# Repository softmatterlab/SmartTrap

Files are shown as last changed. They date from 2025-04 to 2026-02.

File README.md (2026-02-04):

# SmartTrap system

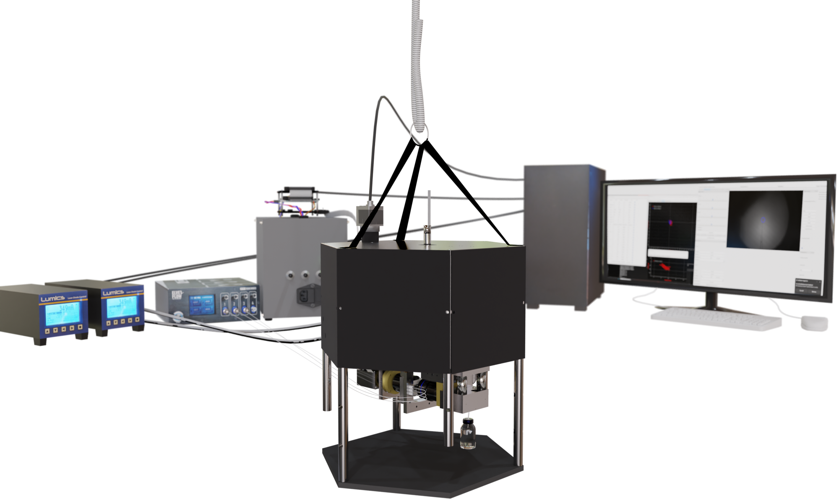
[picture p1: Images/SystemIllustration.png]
Illustration of the SmartTrap system


This GitHub page describes the SmartTrap system, including how to assemble and set up your own system.
The system is described in our publication, currently on arXiv: <https://doi.org/10.48550/arXiv.2505.05290> 
The SmartTrap system is capable of running advanced experiments such as, single molecule force spectroscopy, autonomously for over 10 hours. It can automatically trap particles and perform a growing range of measurements. Schematics and software are accessible here making it easy to build you own SmartTrap or adapt parts of it to your own system. 

## Hardware
The SmartTrap system is based on the MiniTweezers optical tweezers instrument, details of which you can find here: <http://tweezerslab.unipr.it/cgi-bin/home.pl>
Here, we provide lists of the components you need to assemble your own system along with guidlines on assembly and installation of the system.

### Components
The components of the system are split into separate units, instrument, electronics controller etc. Files listing the different components are found in the components folder.

### Assembly instructions
The assembly of the instrument is outlined in the [FullAssembly video](<Supplementary Videos/FullAssembly.mp4>). 

## Electronics
The optical tweezers instrument is controlled by a custom electronics controller. This controller consists of 3 separate circuit boards (PCBs) which are connected together via ribbon cables.

### Circuit boards
The 3 circuit boards of the controller are listed below.
- PCB 1 - Microcontroller board: Hosts the microcontroller which is an Arduino Portenta H7. This board is connected to both the other boards and the host computer.
- PCB 2 - Sensor board: This board connects to the various sensors, amplifying and digitizing the signals. Connected to the microcontroller board with a ribbon cable.
- PCB 3 - Actuator board: Connects to the motors and piezo actuators which moves the sample stage as well as the laser positions. Connected to the microcontroller board with a ribbon cable.

The Bill of Materials (BOM) files are in the [components folder](Components/) and the schematics of the boards can be found in [Instrument Schematics folder](<Instrument Schematics/>).

### Firmware
The firmware is the program running on the controller, specifically the microcontroller, to steer it. It needs to be installed for the controller to work. The files can be found in the [Firmware](Firmware/)  on this github page.
To install (flash) the firmware onto the controller do the following.

 - Connect the microcontroller to the host computer. For this use a USB-C cable.
 - Download the [Firmware folder](Firmware/).
 - Open the folder in an arduino IDE. We recommend using Arduinos own IDE which you can find here: <https://www.arduino.cc/en/software/>
 - Under tools select the arduino portenta H7 board and the correct COM port (should show up as Arduino Portenta h7).
 - Compile and upload the firmware by pressing the upload button in the top left corner of the IDE. There are a few extra packages needed to compile the software, if these are not installed the arduino IDE will automatically prompt you to install them.
Once the firmware is correctly uploaded, and the microcontroller is connected to both the controller PCB and the host computer, a green light will be flashing periodically on the microcontroller.

Note that other IDEs, such as Visual Studio Code, are possible to use, but may require a bit more work to set up.

### Controllers and drivers
The SmartTrap system combines a central instrument controller with several independent devices, each with its own hardware controller and corresponding Python driver. All drivers follow a Python protocol, so replacing hardware requires only implementing the correct interface and updating the create_devices function in the smarttrap_config.py file to use your own different device. Further details can be found in the Software folder.

- **Optical tweezers instrument** - The instrument is controlled using the custom controller. This provides also control of the motors, laser movement and sensor readings.
  - Hardware: Custom electronics controller. Controls the motors, laser positioning and reads the various photosensors.
  - Driver: Communicates with the host computer with serial USB. The different subsystems, sample stage motors, laser actuators and photosensors, are each controlled by separate classes allowing them to be easily replaced without replacing the entire controller if need be.
- **Camera** - The camera is monitored directly in the user interface. From the interface one can record videos, note that the camera feed is used in the autonomous protocols.
  - Hardware: Two options currently implemented: Thorlabs scientific cameras and Basler cameras. 
  - Driver: Connects automatically to the camera from the chosen suppliers. Other cameras can be implemented using the interface in camera_controls. The Basler cameras requires the PyPylon package while the Thorlabs cameras require installing the [thorlabs SDK](<https://www.thorlabs.com/software_pages/ViewSoftwarePage.cfm?Code=ThorCam>)
- **Laser power control** - Enables adjusting the power of the two lasers directly from the user interface as well as during autonomous protocols.
  -  Hardware: Uses an OSTech laser diode driver and TEC controller [ds11-la0.5v14-pa02v14-t8545-691](<https://www.ostech.de/en/products/laser-drivers/ds11-t85/691>).
  -  Driver: Uses serial communications, integrated in the OSTech laser.
- **Microfluidics** - The microfluidics is used to deliver particles into the system. It is possible to use manually operated syringes as well, but full digital control is necessary for autonomous procedures.
  - Hardware: Pump and valves used are from [ElveFlow](<https://elveflow.com/>), in particular the OB1 microfluidics pump and the Mux Wire V3 valve controller.
  - Driver: Requires ElveFlows proprietary software as well as the  the [LabView runtime engine](<https://www.ni.com/en/support/downloads/software-products/download.labview-runtime.html?srsltid=AfmBOoqhYo82koPNAGyVOaWM6Thr4NwTCO1KBI9eCecb0INE0mCxeVmB#569345>)
- **Micropipette** The suction of the micropipette can be toggled by activating the pump connected to it.
  - Hardware: Uses a pump powered by a dc motor, D2028B from SparkFun Electronics. This is controlled by a separate power supply, TENMA 72-2540
  - Driver: Python driver with the ability to set the power of the pump and toggle the suction on and off.
- **Motorized objective movement**- This is an optional addition and allows the user to move the objectives from the user interface for adjusting focus.
  - Hardware: Is an arduino UNO. The program for it can be found in the firmware folder.
  - Driver: Python driver communicating using serial USB. Allows for moving the objective in either long or short steps closer to or away from the chamber.
- **Pipette puller** A separate device used to make the micropipettes by heating and pulling on glass microcapillaries.
  - Hardware: Custom desgined, see pipette puller section. Powered by a TENMA 72-2540 power supply.
  - Driver: Runs in a separate graphical user interface in which the parameters of the heating can be tuned to get suitable size of the pipettes.

### Connecting the controllers
Connecting the various controllers is simple. All connect to the host computer using USB. Importantly you will need to configure the softwware to know which COM port is used for which device. This is configured in the smarttrap_config.py by updating the appropriate port, which ports are used can be found in the device manager if you are using a windows pc.

## Main program
The main program runs on the host computer and is used to steer the entire system. It includes a graphical user interface (GUI) and the fully autonomous protocols.

### Installation
To install the main program first download the files in the Software folder of the github. It is recommended to use Anaconda (<https://www.anaconda.com/>) set up a separate python environment for the SmartTrap. The system has been tested on Windows 11, compatability with other operating systems has not been tested.
The software is tested with Python 3.13 as well as a computer running Windows 11 and a CUDA ready graphics card. Older and newer versions of python will likely work if they support the required packages, but have not been extensively tested.
Once a python environment has been created, do the following to install the required packages. 
- Open a terminal in the desired environment.
- Navigate to the target folder with the downloaded files.
- Run the command: "python install_auto.py" to install the required packages.
  - Recommended: Install pytorch with CUDA support,
   - To install cuda on windows <https://docs.nvidia.com/cuda/cuda-installation-guide-microsoft-windows/> Install cuda prior to running the install command to automatically install pytorch with cuda support.

The software needs to know which device is connected to which port. To check this open up the windows device manager to check the COM ports.
Then change in the config.py file and insert the appropriate COM ports to have the software automatically connect to the devices. Note that port numbers can change, for instance if the computer is updated, if this happens just update the config file accordingly.

### Starting the software
Once the installation is complete the program is started from the command prompt with the command:
"python main.py"
This will start the program and open the graphical user interfaces. To run the command ensure that you have the correct python environment and that the command prompt is in the same folder as the software.

### Using the interface
The various controls of the instrument are divided into different by different widgets. These are essentially small windows. The most central ones are described below.

**The main window**

The main window contains the camera view as a central component and most of the different widgets are docked in it by default.
From the main window you can open the different widgets and perform various actions. By selecting the different mouse tools you can use your mouse to directly control the interfaces, by for instance selecting the motors you can click and drag on the screen to move the sample around.

**Protocols widget**

This widget is used to manually specify to the instrument which laser protocol to run. These protocols run on the microcontroller and steers the lasers, for instance moving the optical trap at a fix speed between two different positions.
To set the parameters first write in the values you want and then hit set parameters. You can see the current values of the parameters in the column to the right.
To start a protocol hit the "toggle protocol" button.

**Mouse tools**

There are several different tools you can use with the mouse to interact with the instrument based on what is seen on the camera feed. These tools are found and selected in the top left of the interface. With these you can for instance zoom in the camera view to an area of interest, measure distances, move the lasers and move the sample stage by clikcing and dragging.

**Plotting**

To plot and monitor signals, such as the forces, open a plotting window by opening the "windows" drop down menu and selecting "live plotter".
This will open the default plotting tool which plots the force along the y-axis as function of time. To change which signals are plotted click "plot 1" in the plot window to open the plot options menu. There you can find x-data and y-data. Click these to select which signal to plot on the y-axis and which to plot on the x-axis.
You can add more separate plots by clicking the "add plot" button.

There are also several plot presets which you can select directly from the windows dropdown menu in the main interfaces. These are; force PSDs, positions PSDs and force-distance X and Y. 

It is possible to export both data and graphs directly from the plotting windows. To do this right click on the plot and select the export option.

**Recording data**

To record data hit the record data button at the top right corner of the interface. It turns green automatically when data is recording.
Likewise, to record videos, hit the record video at the top left of the screen. 
You can select where to save the data by using the file drop down menu and selecting the "save data path" option. Under the "file" menu you can also select the format of videos, images and the data saved.

**Motorized stage movement**

There are two primary methods for moving the motors manually. You can use the mouse tool to move the motors by clicking and dragging, or you can use the motor control widget. From this widget you can move in your specified direction at a specific speed. The movement speed can be set by typing the desired movement speed in the entry bar or selecting one of the preset speeds.

Under the actions tab at the top of the interface you can save positions in the chamber, when you do this you also name the position. You find also the "go to saved position" option in the actions tab which lets you move to one of the saved positions.

**Laser movement**

You can manually control the laser movement from the laser movement widget. To do this use the sliders. There are 4 sliders, one per laser and axis. The sliders will also move if there is a protocol running indiciating how the lasers move. From this widget you can toggle the automatic laser alignment.

**Autonomous control**

To monitor and toggle the various autonomous protocols use the autocontroller widget. This is opened from the windows drop down menu. With the autocontroller widget you can both monitor and toggle the various autonomous protocols and use some of the autonomous subroutines (e.g. putting a particle in the pipette).

#### Testing the software

You can run the interface also without any of the devices connected. To do this follow the instructions to start the software, but add the extra argument -testmode by running the command:
"python main.py -testmode"
This will create testdrivers for the different devices which act similarily to the real devices from a software perspective, but are not connected to any physical hardware.
These testdriverds can also be used to test the functionality of just one or two devices separately from the rest of the system during development.

### Autonomous control
There are various autonomous protocols that the instrument can execute.
You can choose to run entire experiments, such as a single molecule force spectroscopy. Alternatively you can run just one of the subroutines, such as the automatic trapping.

### Neural networks
The weight of the networks needed for the automation are stored in the folder /NeuralNetworks and the weights of a pretrained network are available in the file YOLOV5Weights.pt. 
Note that other custom trained networks can be loaded directly from the user interface. 

# Expanding on the software
The software provided here is open source and as such you are free to download and modify it to your own needs.

## Adapting the software to other systems
The software suit, and in particular the interface and its back end, has been designed with the use in other system and experimental procedures in mind. 
The different protocols of the various devices simply needs to be implemented and then you need to adapt the create_devices function in config.py to ensure that your specific device is used.

## Making a sample chamber
The sample chambers used in the SmartTrap are handmade. You can make your own chambers by following the instructions below.

### Items needed
 To make a microfluidics chamber the following is needed. Below are also instructions on how to prepare the parafilm and the glass slides.
 **Tools**:
- Laser cutter
- Hotplate
- Pipette puller
- Scalpel
- Tweezers

**Consumables**:
- Parafilm
- Coverglass slides, thickness 1.5 , 60x24 mm
- Micropipette
- Channel capillaries

Note that both the parafilm and the holes in the coverglasses can be cut with a lasercutter. 

**Cutting parafilm**
First prepare the parafilm by cutting it with the laser cutter. To do this place it stretched horisontally on the laser cutter with the paper peeled off. 
You can for instance use the nescofilm roller from the tweezerlab website <http://tweezerslab.unipr.it/cgi-bin/assemblies.pl/Show?_id=ddd9> for this.

Load the pattern into the laser cutter and position it on the parafilm.
The settings of the laser cutter will depend on the model used. We use vector engraving at ca 50% of max power.

**Preparing the holes of the glass slides**
To make holes in the glass slides you can either use glass drill or a laser cutter.
The optimal settings will depend on the model of the laser cutter. Recommended is to use multiple repetitions.
If you instead use a drill carefully check that all the holes are placed in the correct position.

### Assembling a chamber
To assemble a chamber from the prepared material perform the following steps:

1. Use a scalpel to cut two pieces of parafilm free.  
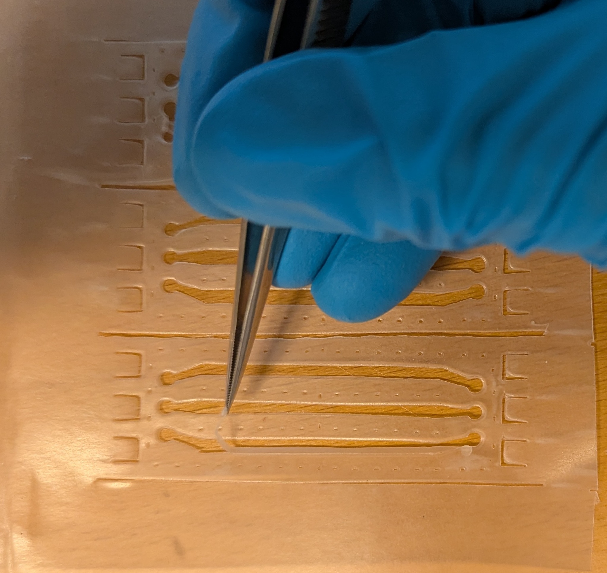
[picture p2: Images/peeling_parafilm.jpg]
Peeling away excess paraflim
   

2. Gently peel away the parafilm covering the channels using the tweezers.

3. Place the parafilm on top of a glass slide with the holes aligned on both sides as per picture.  
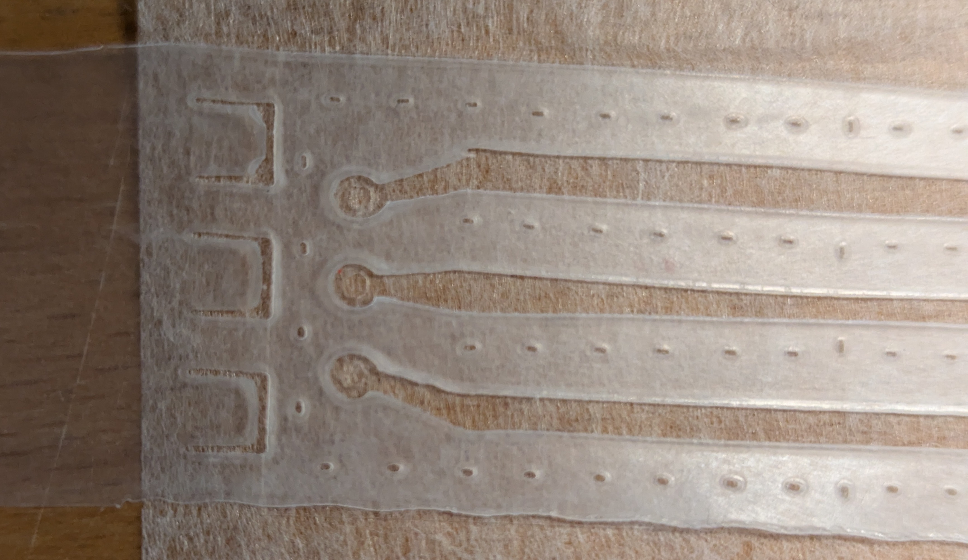
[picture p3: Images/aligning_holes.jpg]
aligning holes
   

4. At this point prepare the pipette following these steps:
   1. Place a single glass capillary centered in the pipette puller.
   2. Gently tighten the four screws to clamp the pipette tight.  
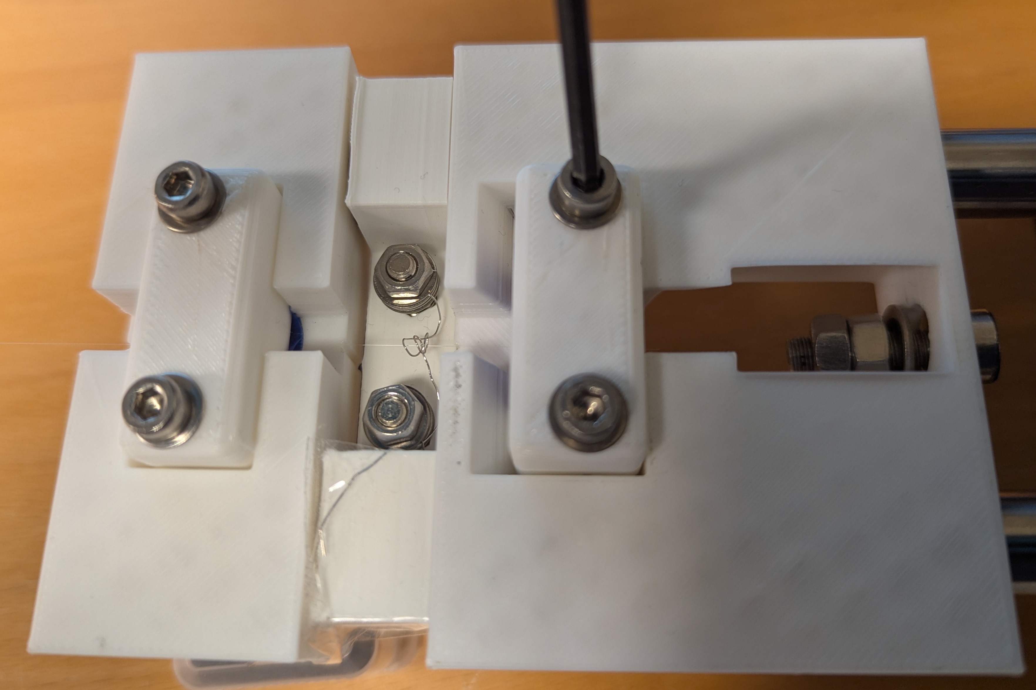
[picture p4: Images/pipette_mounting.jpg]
mounting pipette
      
   3. Carefully raise the pipette puller to a standing position.
   4. Toggle the pipette pulling protocol in the pipette puller program. [Watch demo video](<Supplementary Videos/pipette pulling.mp4>)
     NOTE: When a pipette is pulled two sharp ends are made, only the bottom part is used since the top is most often closed up completely. Therefore it needs to be cut off if the same capillary is used to make multiple pipettes. 

5. Next, place the micropipette in the center of the chamber and the capillaries next to it. Pipette and the capillary openings should be near the central chamber’s center as shown in the picture.  
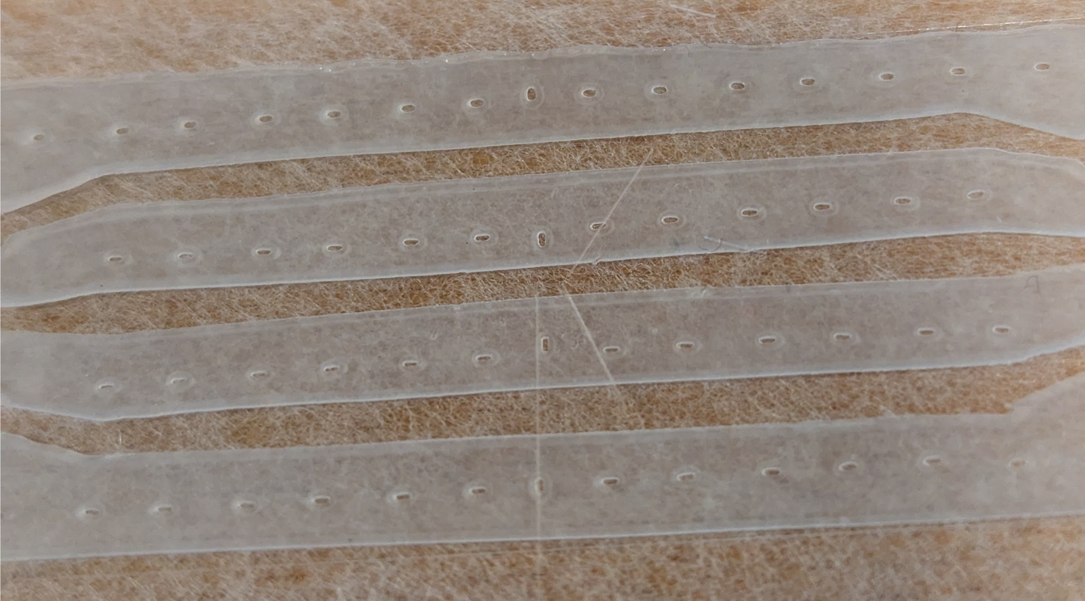
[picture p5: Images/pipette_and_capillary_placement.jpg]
pipette and capillary placed
   

6. Place the second sheet of parafilm on top of the first and align it carefully. Be careful not to move the pipette or the capillaries out of place when doing this.  
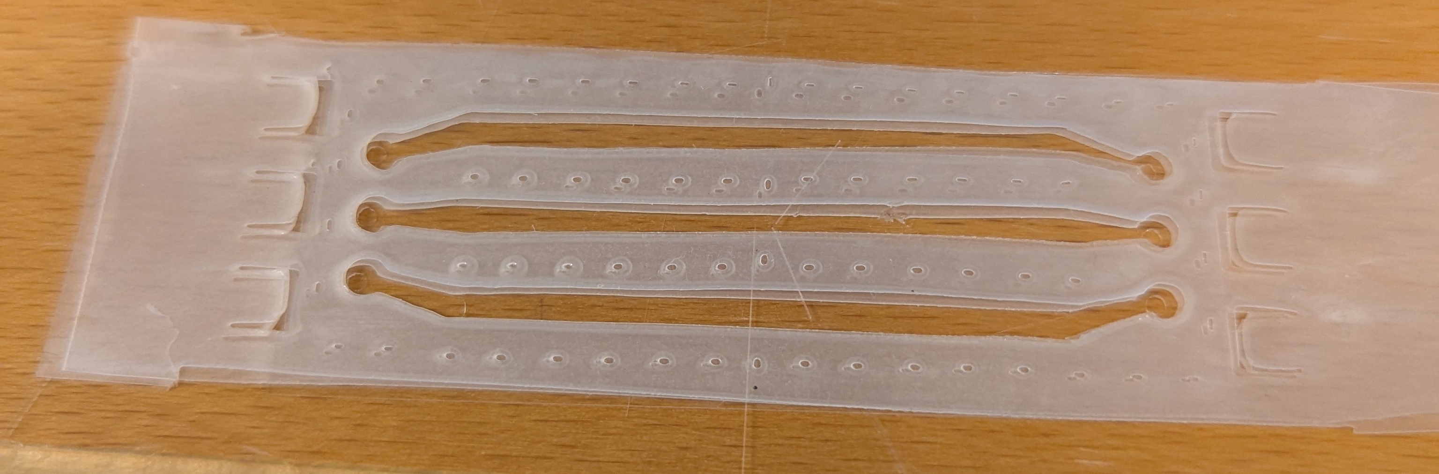
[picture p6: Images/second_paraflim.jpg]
second parafilm
   

7. Place a coverslip without holes on top and align it with the bottom slide.

8. Cut away any excess parafilm.  
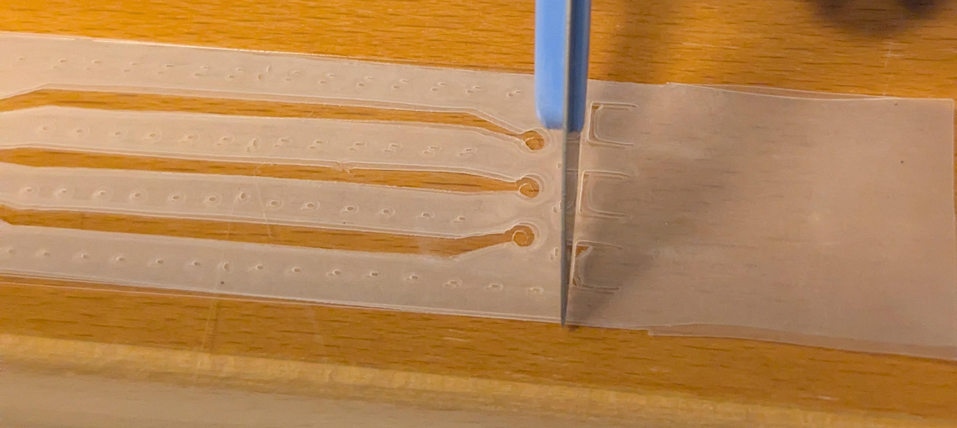
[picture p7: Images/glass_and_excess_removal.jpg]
excess parafilm removed
   

9. Heat the chamber for ~4 minutes at 110 °C on the hotplate with a weight of ~400 g applied.

10. It is recommended to sandwich the chamber between two thicker glass slides for more even weight distribution.

11. Remove the chamber and let it cool off.

### Installing a chamber
To install a chamber first take the sample holder from the system and remove the clamps before starting assembly.

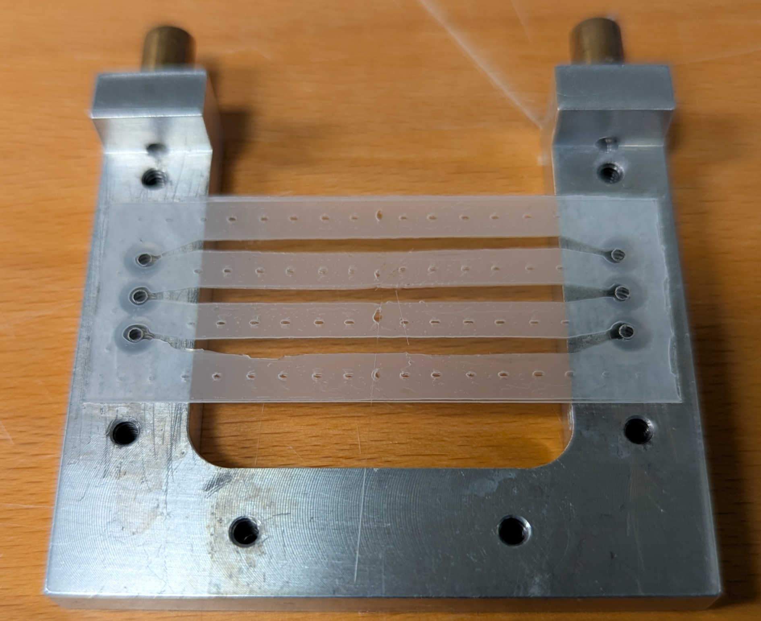
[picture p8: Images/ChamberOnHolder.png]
Chamber mounted
1. Align the chamber with the holder, ensuring that the holes of the chamber are centered at the holes of the holder. 
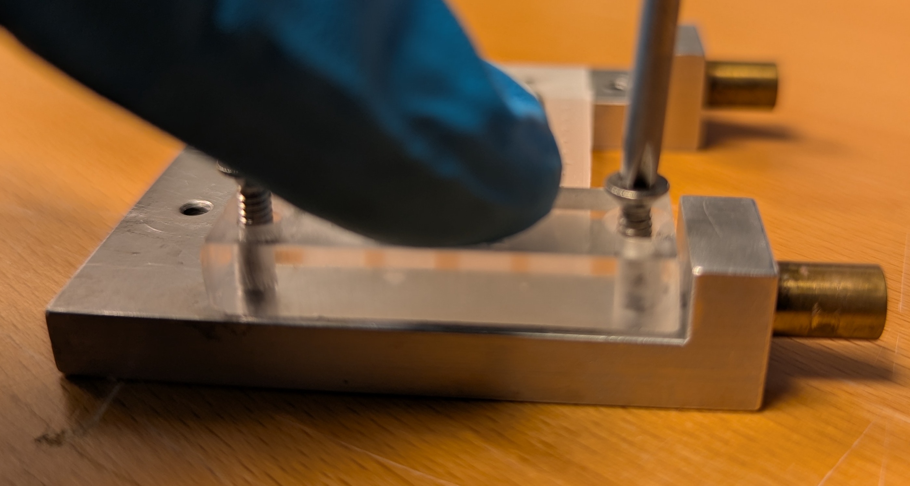
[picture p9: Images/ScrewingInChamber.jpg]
Screwing in chamber
2. Gently mount the two chamber clamps. Keep a finger on the clamp while screwing to ensure an even pressure distribution. 
3. Put the pipette clamp into position and screw the screws halfway in.
4. Put the pipette tubing under the clamp and thread the tubing around the pipette itself. Be careful so as not to break the pipette. Leave ca 5 mm of space betewen the top of the tubing and the chamber bottom.
5. Tighten the pipette clamp.
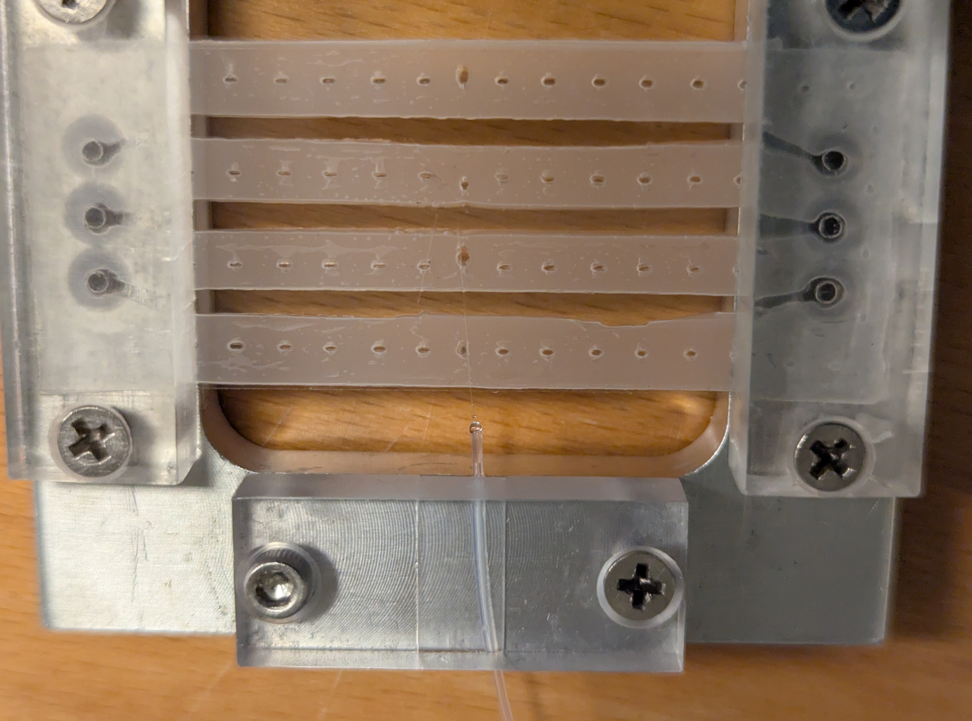
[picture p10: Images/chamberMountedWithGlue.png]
Chamber mounted and glued
6. Add a drop UV-glue to the tip of the tubing. You should be able to see a small amount of glue entering a few millimeters into the tubing. 
7. Cure the UV-glue using a UV-lamp.
8. Install the microfluidics screw connectors.
9. Connect the microfluidics tubing. Make sure the flow is directed so that the capillaries in the correct direction....
10. Flow buffer into the chamber and make sure there are no bubbles. If there are bubbles in the chamber try to remove them by briefly increasing the flow.
11. If the flow looks good, add a drop of water to the objectives of the system, push the objectives apart and put the chamber in its position as shown.

## Pipette puller
When making chambers you need a micropipette. You can make these yourself from glass capillaries using the pipette puller described here. 

### Puller assembly
Assembly instructions and list of components available in [PipettePuller](<Components/PipettePuller/>).
The puller consists of a metal base with two rods along which the pipette holder can slide.
A platina wire is heated using resistive heating to heat up the capillary and melt it.

### Using the pipette puller
To use the pipette puller first mount a glass capillary in it and connect the cables to the power supply (does not matter which cable goes where since it uses resistive heating). 
Then start the puller software by navigating to the correct folder and running the command "python pipette_puller.py". This will open up a small interface from which you can control the power supply and thereby the pipette puller heating.
The heating protocol is run by hitting the start protocol button. This will start the heating. 

The parameters used for the pulling may need to be tuned to optimize the shape of the pipette. In general, the faster the pulling the smaller the pipette opening (and the longer the larger the opening). Increasing the maximum allowed current of the puller will decrease the pulling time.

# Supplementary Videos
The /Supplementary Videos folder contains 5 videos which showcase the capabilites of the SmartTrap system.

# License
This project is licensed under the MIT License - see the LICENSE file for details.

# Cite us!
You can find more information in our paper:
<https://doi.org/10.48550/arXiv.2505.05290>
```
Martin Selin, Antonio Ciarlo, Giuseppe Pesce, Lars Bengtsson, Joan
Camunas-Soler, Vinoth Sundar Rajan, Fredrik Westerlund, L. Marcus Wil-
helmsson, Isabel Pastor, Felix Ritort, Steven B. Smith, Carlos Bustamante,
and Giovanni Volpe. SmartTrap: Automated Precision Experiments with
Optical Tweezers, May 2025. arXiv:2505.05290 [physics]
```

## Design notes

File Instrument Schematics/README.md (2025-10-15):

# Electronics of the instrument
Schematics of the controller are in the PDFs found here. Follow the steps below to connect the controller to your instrument and your controller power supply.

## Connecting the controller
The controller consists of a stack of 3 separate boards which are connected together using ribbon cables. To connect the controller follow the steps below. All the images are oriented in the same direction.
### Actuator board
Place this board on the bottom of your controller stack
- Connects to t 3 different power cables from the power supply. The 150 V (for the piezos) the, +- 15V (4 cables connector) and the 5V & 12V (3 cables connector)
- Two ribbon cables to the instrument, one for the motors (34 connectors) and one for the piezos
- Connects to the Main control board with a 34 connector ribbon cable

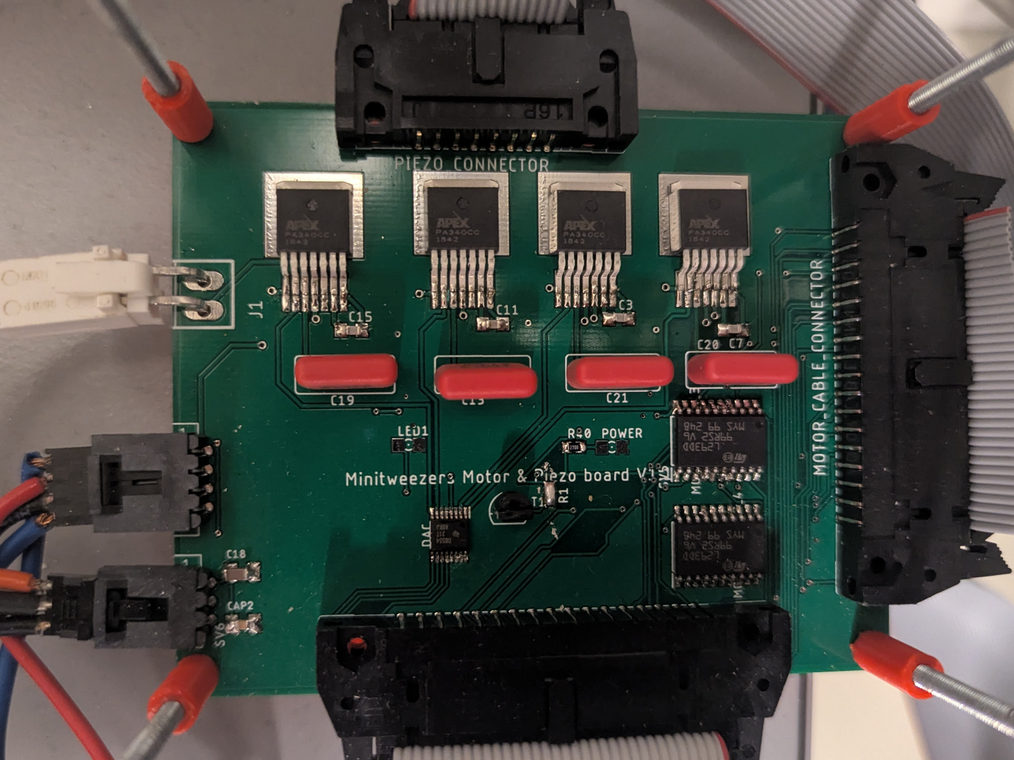
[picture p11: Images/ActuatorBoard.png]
ActuatorBoard


### Sensor board
Place this board in the middle of your controller stack
- Two power cables power it +- 15V (4 cables connector) and the 5V & 12V (3 cables connector)
- Connects to the instrument with 4 cables, one per set of PSDs, on the short end (left short end in the picture). From top to bottom in the picture these are:
  - Force B
  - Position B
  - Poistion A
  - Force A.

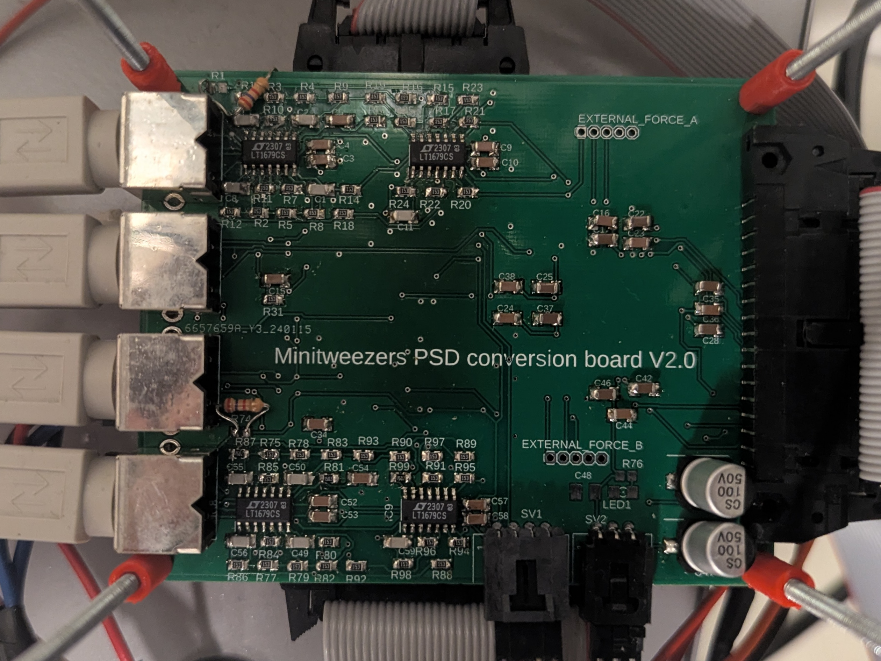
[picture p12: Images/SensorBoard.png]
SensorBoard


### Microcontroller board
Place this board on top of you controller stack.
- Connect it to the Sensor board and the actuator board using 34 connector ribbon cables. The sensor board connects to the short end of the board and the actuator board to the long end.
- Connect it to the host computer with a USB-C cable attached to the arduino portenta. The ARDUINO should be oriented as in the picture below. It will start blinking green when connected to the computer and the program is running.

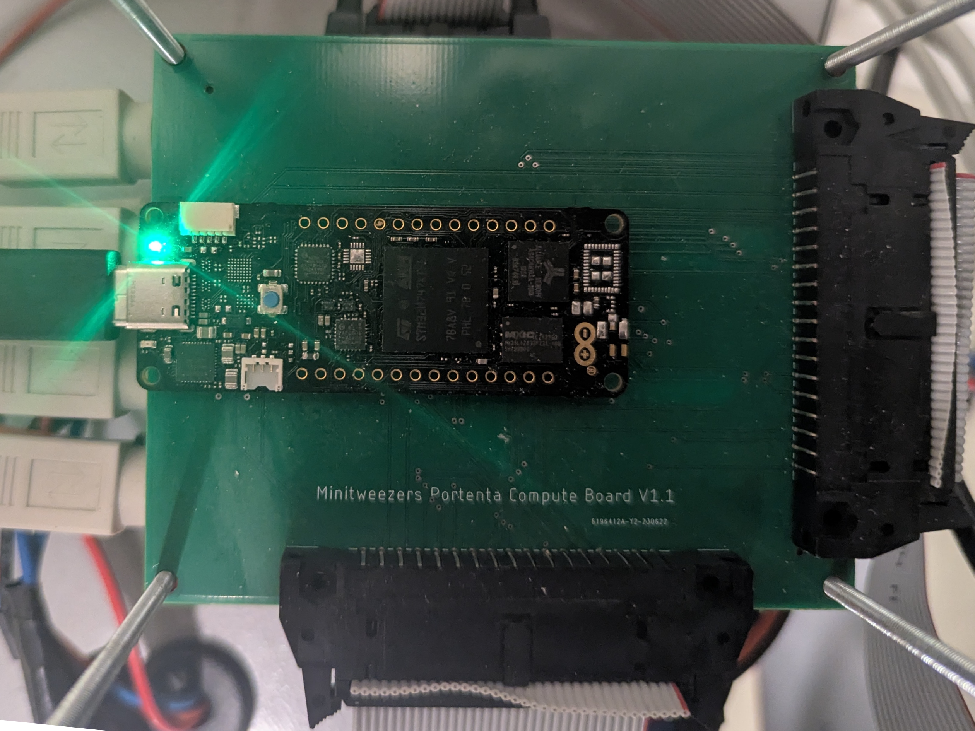
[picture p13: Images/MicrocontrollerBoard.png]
ControllerBoard


## Controller stand
To mount the controller boards you can 3D print the controller stand from the stl file ControllerStand.
It is recommended to also print the PCB spacers to put between the different PCBs. Use a set of long (ca 80 mm) M2 screws to mount the different boards and spacers effectively as in the pictures.

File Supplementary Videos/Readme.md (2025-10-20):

# Here are the supplementary videos:
The videos showcases the operation of the autonomous system.

## 1 - 3D tracking of the pipette

This video is a screen recording of the camera view in the user interface with real-time tracking visualization turned on. The video shows where the program detects the pipette and the particle. This is done while simultaneously moving the pipette with the particle in and out of focus, estimating the particle focal position.

https://github.com/user-attachments/assets/bb30b676-af74-496c-bb91-06eaeb164970

## 2 - Particle characterization 

The video shows the autonomous particle characterization being performed. The video starts with the instrument moving to a capillary to trap a particle. The first particle trapped is one of the target particles, which is determined by the autonomous algorithm based on it being larger than a certain threshold. Since it is one of the target particles the hydrodynamic radius is measured by moving it between two fixed positions in the sample while recording the forces and motor movement. Once the measurement is finished the microfluidic pump connected to the central chamber is turned on creating a flow which removes the trapped particle. Next, another particle is trapped. By chance this is a small particle, which should not be characterized, therefore it is immediately removed, again using the pump connected to the central chamber. Next, a situation in which multiple particles are trapped is shown. In this case the software detects that the focal position is offset compared to what is expected from a single particle and therefore the particles are removed even though the profile size match those of the target particles. 

Lastly, several experiments are displayed at a high speed with a timer added to illustrate how the system can run for extended times characterizing dozens of particles.

The recording is performed using the interface itself rather than recording the screen itself. This gives slightly higher video quality than a screen recording.

https://github.com/user-attachments/assets/05ffb2d9-0af1-4bef-83d9-a1c86171ede3

## 3 - Autonomous DNA pulling

Video illustrating the autonomous DNA pulling. First, a recording of a single autonomous pulling is shown starting with an empty chamber, without particles in either trap or pipette. This part of the video is commented and is a recorded camera feed showing all the different steps of the autonomous pulling process. Starting with checking the pipette, followed by trapping of the streptadavin particle and positioning of this in the pipette. This is followed by the trapping of a particle with DNA which is then attached to the particle in the pipette where after the experiment measurement is perfromed. After this first pulling, the video shows the full graphical user interface while the program performs a large number of pullings autonomously. This part of the video is shown at increased speed (to limit the duration of the video) and also the real-time plotting is shown. At the end a recording from a 10 hour continuous experiment is shown. This is shown at 600 times normal speed (10 minutes shown in 1 second) to showcase long term operation.

https://github.com/user-attachments/assets/ae2c6801-45a3-41bb-a317-445c46f49120

## 4 - Red blood cells
The videos shows how the red blood cell experiments are performed by the instrument. The video is a screen recording of the GUI and also includes a timer. After a cell has been trapped, initially at low power, cells profile is recorded in a video. Then the trapping power is briefly increased and the cell profile at higher power is recorded in another video. Thereafter the trapping power is reduced and the process repeated four more times at increasingly high powers. Thereafter the cell is removed by a flow. Since there are cells dispersed in the medium the flow is also used to bring new cells into view which are trapped and measured. If by chance there are no cells in view after flowing new medium then the flow is briefly turned on again.

https://github.com/user-attachments/assets/55d9182e-a0de-4d83-9847-974e01d260b4

## 5 - Electrostatic repulsion
Showcase of how electrostatic repulsions can be measured autonomously. When the video starts there is nothing in either trap or pipette. The program first focuses the pipette and checks its content. Next it moves to the capillary, turns on the microfluidic pump and traps a particle. The trapped particle is then placed in the pipette. After confirming that the particle has successfully transferred to the pipette, a second particle is trapped and brought to the pipette. The particle in the trap is aligned to the particle in the pipette. The trapped particle is pushed towards the particle in the pipette by moving the trap to find appropriate limits for the measurement protocol. Next the protocol and recording of data (both force and video) are started. At this stage the program zooms in on the two particles to limit the size of the videos. Once the measurement is completed, a strong flow removes both particles resetting the experiment and preparing the system for another measurement.

https://github.com/user-attachments/assets/04064912-fe21-4e13-9837-17cc39bfbc88

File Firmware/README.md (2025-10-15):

# Firmware for the arduino
This folder contains the Arduino Portenta firmware. To install download the folder and open the project in the Arduino IDE (https://www.arduino.cc/en/software/). Further instructions are available in the GitHub main page.

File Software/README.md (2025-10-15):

# This folder contains all the software needed for running the SmartTrap interface

The different modules handle different parts of the instrument controls.

To use the software with other than the default devices (e.g. a camera from a different manufacuter) implement the protocol of the corresponding device. 
These protocols need to be implemented for the different devices to work with the interface and the autonomous control functions. In the case of camera implement the "CameraProtocol" from camera_controls.py and update the create_controls function.

Below we describe briefly the functionality of the different modules. More detailed descriptions are available in the separate modules and examples of how to use them are in the Examples folder.

## install_auto
Run this file to install the packages used by the SmartTrap system.

## main
Run this file to start the program with the interface. Adding the flag -testmode will let you run it without any devices connected.

## smarttrap_interface
This contains the graphical user interface (GUI) of the smarttrap system. The entire system can be controlled using the GUI.
Contains the following two classes:
- **MainWindow** - The MainWindow is a subclass of QMainWindow and contains the main GUI.
- **ScreenWorker** - class is used to update the contents of the camera screen, displaying the camera feed and drawing things like particle markers.

### Using the software with other devices
In the create_controllers function the different devices are connected. To use your own devices, create a new create_controllers functions.

## camera_controls
Contains the classes used to interface the cameras and connect these to the user interface. Also has the functionality used to record videos.

The module contains the following classes
- **CameraClicks** - Class used to allow users to click and drag to set the area of interest of the camera. Implements the MouseTool protocol.
- **CameraMeasurement** - Used to measure distance on screen by left and right clicking. Implements the MouseTool protocol.
- **CameraProtocol** - The protocol that camera objects need to implement to function together with the rest of the program.
- **TestCamera** - A mock implementation of CameraProtocol used for testing software without any (physical) camera connected.
- **CameraThread** - A thread which runs in the background and continuously captures images using the connected camera.
- **VideoWriterThread** - Runs in the background and records videos on demand.

## data_saver
This module contains a thread saves data into files when prompted to. By running in a separate thread this limits the risk of the saving of large files interfering with other processes.

Contains the following classes:
- **SaverThreadInterface** - Interface which needs to be implemented by any DataSaver class to function with the interface.
- **DataSaverThread** - Implementation of SaverThreadInterface which is used in SmartTrap to efficiently save the data.

## control_parameters
This file contains classes and functions used to control the various devices and handle data.

Contains the following classes:
- **DataChannel** - A class which stores the data and in an array of fixed length and which can be easily, and efficiently, updated with new data.
- **ControlParametersViewer** - Wdiget which displays the current values of the various control parameters. Used primarily in development to monitor the parameters.
- **CurrentValueWindow** - Class which is a PyQT widget that is used to monitor the various data channels, their current values and an rolling average of the current values. The widget can also be used to select which channels are saved when saving.
- 

## microfluidics_controllers
This file defines the interfaces used for the 3 different microfluidics control devices; the pump, the valves and the pipette pump.
- **MicrofluidicsController (Protocol)** – Interface for multi-channel pressure controllers (connect/disconnect, set/get pressure, channel count).  
- **ValveController (Protocol)** – Interface for valve array controllers (connect, connection status, toggle/query valves).  
- **PipettePump (Protocol)** – Interface for pipette pump PSUs (connect/disconnect, power control, suction on/off, status).  
- **TestMicrofluidicsController** – Mock 3-channel pressure controller (0–2000 mbar, 1-based indexing) for testing without hardware.  
- **TestValveController** – Mock valve controller storing in-memory valve states for UI/logic testing.  
- **TestPipettePump** – Mock pipette pump PSU with % power setting and suction state simulation.  
- **MicrofluidicsMonitorThread** – QThread that syncs target/current pressures, valve states, and pipette pump power with shared state every 500 ms.  
- **ConfigurePumpWidget** – Qt form to configure channel/valve assignments and per-channel max pressures for autonomous use.  
- **MicrofluidicsControllerWidget** – Qt live control panel for setting pressures, toggling valves, and controlling pipette pump with auto-refresh.  

## motor_controls
The files defining the controls of the motors. This module defines protocol interfaces and lightweight test implementations for a 3-axis motor stage and an objective stepper, plus Qt tools/widgets for manual and mouse-driven control.

#### Protocols
- **Motor (Protocol)** – Abstract 3-axis stage motor (set/get speed, absolute move to position, velocity move, position readout, stop, is_moving).
- **ObjectiveMovement (Protocol)** – Objective actuator with slow/fast motion toward/away from the sample (connect/status + 4 directional presets).

#### Test Implementations
- **TestMotorController** – In-memory 3-axis stage with nominal speed and instant absolute moves; `move_at_speed` integrates a 1-second step for demo.
- **TestObjectiveMovement** – In-memory objective actuator that logs slow/fast moves and connection state.

#### UI & Tools
- **MotorControllerWindow (Qt)** – Manual control panel: speed presets (1/10/100 µm/s), arrow keys for x and y movement and PgUp/PgDn for Z, and a sample LED toggle bound to `c_p['blue_led']`.
- **MotorMouseMove (MouseTool)** – Mouse-driven movement: click-to-move, right-drag for X and Y velocity control, middle-drag for Z.
- **ObjectiveStepperControllerToolbar (Qt)** – Toolbar with slow/fast actions toward/away from sample for the objective stepper.

> Shared state: Components expect a `c_p` dict (e.g., `blue_led`, `mouse_params`, `camera_width/height`, `AOI`, `image_scale`, `ticks_per_pixel`), and real controllers should implement the `Motor` / `ObjectiveMovement` protocols.

## mouse_tools
This module defines a lightweight `MouseTool` protocol for PyQt/PySide applications.  
It standardizes how tools handle mouse events and optional custom drawing.

#### Protocol
- **MouseTool (Protocol)** – Abstract interface for interactive tools:
  - `mouseMove`, `mousePress`, `mouseRelease`, `mouseDoubleClick` – Mouse event hooks.  
  - `draw(qp, ...)` – Optional rendering on a `QPainter` context.  
  - `getToolName()` – Short, human-readable name of the tool.  
  - `getToolTip()` – Tooltip/description of the tool’s functionality.

## live_plots
This module provides a customizable PyQt6/pyqtgraph plotting window designed for live data visualization during operation. All the different data_channels in the data_channels can be easily plotted and monotired at will.

- **Core class – `PlotWindow`**  
  - Inherits `QMainWindow`.  
  - Manages multiple plots with per-trace metadata stored in a shared `plot_data` dict (`x`, `y`, `pen`, `L`, `sub_sample`, `averaging`).  
  - Updates plots on a `QTimer` loop (`update_plot_data`) pulling from a user-provided `data` mapping.  
  - Designed for `data[key]` objects exposing:  
    - `.get_data(n)` / `.get_data_spaced(n, step)`  
    - `.unit` (for axis labels)  
    - `.index` (for alignment logic).  

- **Supporting dialogs**  
  - `PlotAxisWindow` – manual x/y axis bounds.  
  - `PlotLengthWindow` – number of points retained per trace.  
  - `PlotSubsamplehWindow` – subsampling/averaging interval per trace.  

- **Customization hooks**  
  - Per-trace styling: line color, marker symbol, symbol color.  
  - Background color presets.  
  - Aspect ratio locking.  
  - Non-overlapping averaging helper (`non_overlapping_average`).  

- **Programmer notes**  
  - Plots are registered dynamically with `add_plot(x_key, y_key)`.  
  - Each plot can be removed via `delete_plot(idx)`.  
  - Menus are auto-rebuilt from `plot_data` state (`create_plot_menus`).  
  - Designed to integrate with an external control dict (`c_p`) that tracks program state (e.g. `c_p['program_running']`).  

This structure makes it easy to embed real-time plotting into larger control/analysis pipelines while keeping plotting logic isolated and extensible.

## real_time_tracking
This module defines a protocol for particle and pipette tracking (ObjectTracker) together with a simple test implementation (TestTracker) and a PyQt-based control widget (TrackingControlWidget).
This provides both the interface layer and a test harness for integrating tracking models into the larger system.

Contains the following classes:
- **ObjectTracker** - A protocol specifying the expected interface for tracking backends (frame analysis, particle and pipette detection, z-position prediction, and model loading).
- **TestTracker** - A mock tracker that generates random particle positions and simulates pipette detection, useful for testing the GUI without real models.
- **TrackingControlWidget** - Qt widget for toggling tracking modes, loading 2D/z models, and adjusting z-offsets during experiments.

## laser_protocols
The laser protocols define various protocol used to move the lasers in a controlled manner and thereby execute various experimental protocols.
This module defines a common `ExperimentLaserProtocol` interface and several concrete laser-control protocols, plus a Qt widget for selecting, configuring, and running them.

#### Protocol Interface
- **ExperimentLaserProtocol (Protocol)** – Unified API for start/stop/run state, human-readable names/descriptions, and numeric parameters (with descriptions, tooltips, and limits).

#### Protocols
- **ConstantSpeedProtocol** – Moves a laser along a chosen axis at constant speed between two position limits.  
- **Push2ForceProtocol** – Pushes a trapped particle in a given direction until a target force is reached, then stops.  
- **ConstantForceProtocol** – Maintains constant force along X/Y by auto-aligning the second trap and updating force setpoints.  
- **ForceLimitProtocol** – Sweeps between lower/upper force limits at a set speed, reversing direction when thresholds are crossed.  
- **PushAndWaitProtocol** – Pushes toward a force limit, waits for a set duration, then transitions to pulling based on position/force bounds.

#### UI
- **PullingProtocolWidget (Qt)** – Dropdown to pick a protocol, per-parameter editors (labels, tooltips, limits, current values), and a toggle to start/stop; refreshes at 40 ms to call `run_protocol()` while active.

## auto_controller
In this module all the autonomous protocols are defined as well as the corresponding user interface elements. 

- **AutoControllerThread** - Thread which runs the autonomous protocols. This also handles the real-time tracking to simplify synchronization.
- **AutoControlWidget** - A QWidget used to control and monitor the various autonomous protocols. Can also be used to toggle the subroutines which build up the autonomous protocols such as particle trapping.
- **StokesTestWidget** - A small QWidget used to perform the stokes which can be used to calibrate the force detectors or to measure particle diameters.
- **SelectLaserPosition** - A MouseTool used to indicate in the camera feed where the two lasers are. This in turn is used by the autonomous protocols to determine if a particle is trapped or not.
- **AutonomousProtocol** - Interface used for the autonomous protocols. Currently the following protocls are implemented:
  - **DNAPulling** - Autonomous DNA pulling protocol implementing the AuotonomousProtocol.
  - **ElectrostaticRepulsion** - AutonomousProtocol which measures repulsive forces between two charged particles.
  - **ParticleCharacterization** - AutonomousProtocol. Selects a particle within a certain size range (as estimated by the real-time tracking) and measures its hydrodynamic radius using a stokes test.
  - **RBCStretching** - AutonomousProtocol used to measure the stretching of red blood cells by trapping them at various laser powers.

# SmartTrap minitweezers instrument specific files
Certain devices are specific to the SmartTrap system and thus rely on the specific hardware, e.g. specific microfluidics pump.
To use these devices they implement the protocols specified in the above files. By default these are the devices loaded by the program using the create_devices function from the smarttrap_config.py file.

## smarttrap_driver
This module contains the classes that handles communications to and from the SmartTrap electronics controller. Specifically a class which only handles the serial communications running in a separate process and a monitoring thread which parses the commands sent to and from the instrument. During operation both these are running continously.

## basler_cameras
Contains the BaslerCamera class which is an implementaion of the CameraProtocol which can be used with cameras from Basler. Comparible with any camera from Basler which connect using USB. Uses the pypylon package for controlling the camera.

## thorlabs_scientific_cameras
Contains the ThorlabsScientificCamera class which is an implementaion of the CameraProtocol which can be used with cameras from Thorlabs.
To use this you need to have the thorlabs scientific camera sdk installed see <https://www.thorlabs.com/software_pages/ViewSoftwarePage.cfm?Code=ThorCam>

## elvesys_pump
Contains an implementation of the microfluidics controllers that work with the OB1 micrfluidics controller from elvesys as well as their microfluidics valve.

## OSTech_laser_controller
Implementations of the lasercontroller that work with laser current drivers from OSTech.

## smarttrap_tracker
The default tracking used in the SmartTrap system. Here the real-time tracking interfaces is implemented to work with yolov5 and the convoluitonal neural network that monitors the z-position.

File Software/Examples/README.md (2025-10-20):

# These are examples of how use the various devices
The examples provide minimal codes for testing the various devices and interfaces. The various files shows how to connect to the various devices and execute basic commands, e.g. taking a picture with the camera.

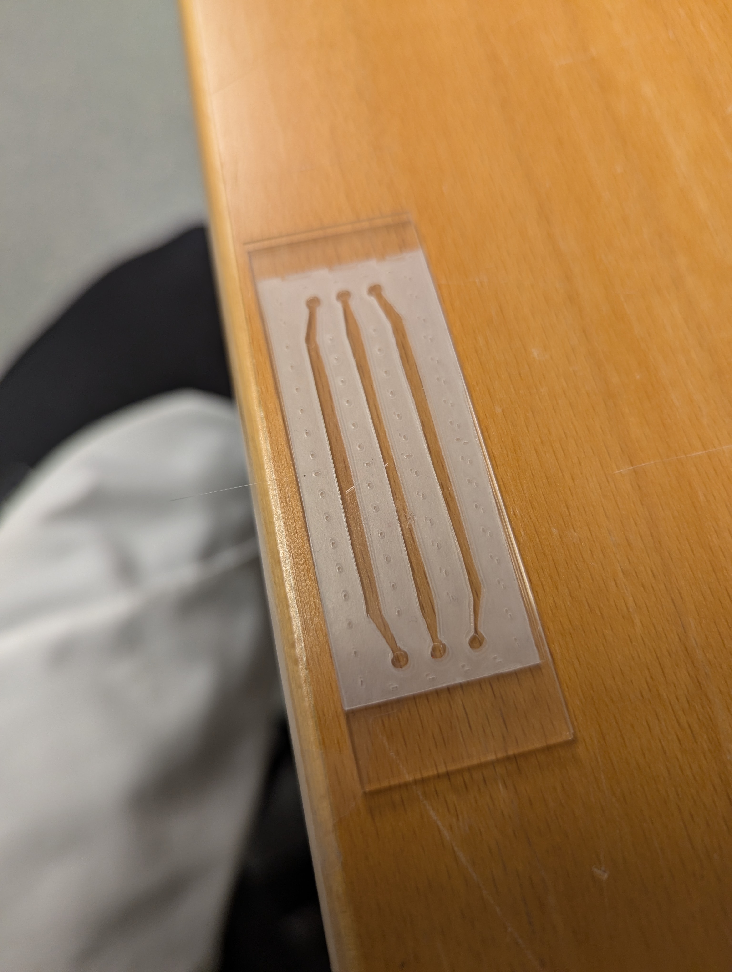
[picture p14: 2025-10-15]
Images/chamber_in_glass.jpg

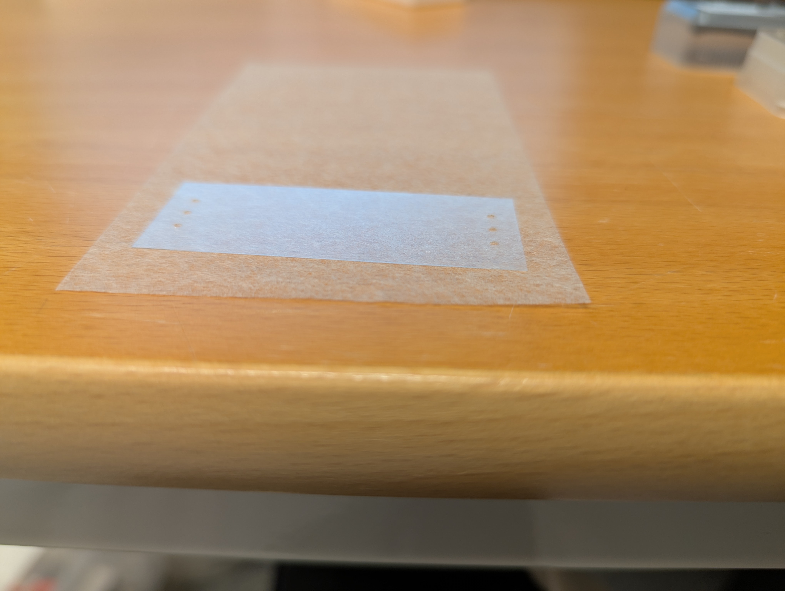
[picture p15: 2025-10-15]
Images/glass_with_holes.jpg

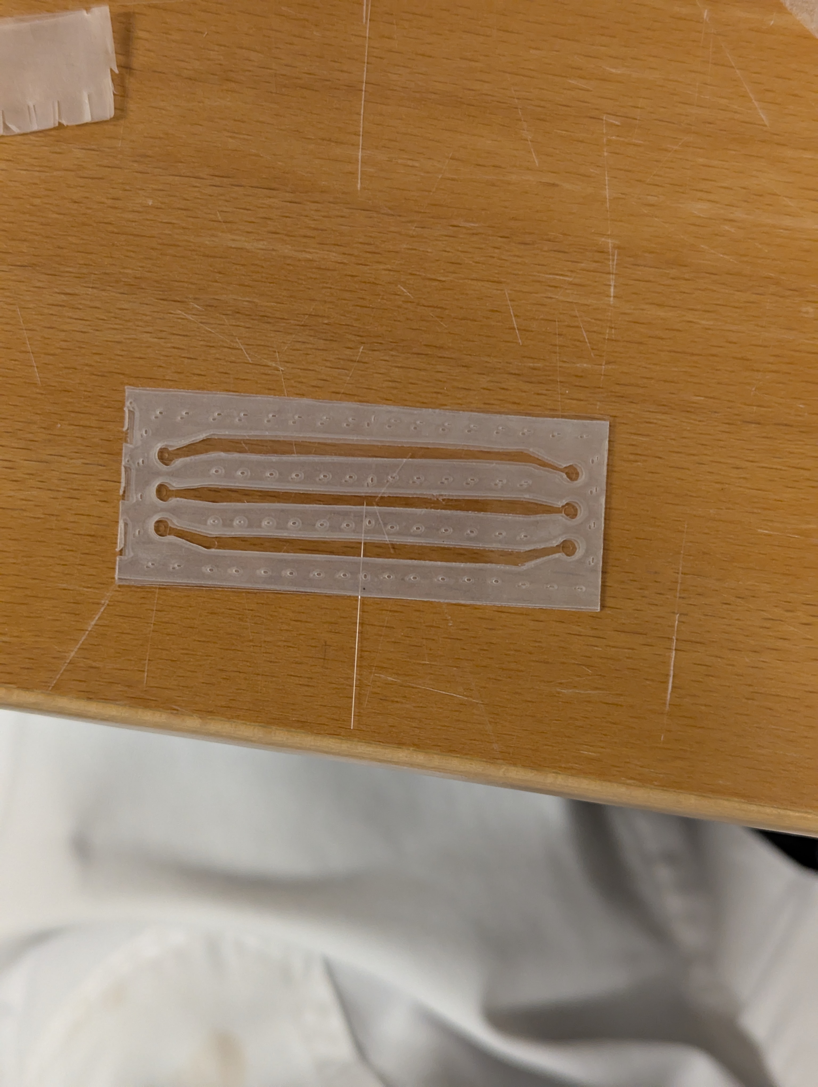
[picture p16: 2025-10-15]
Images/unheated_chamber.jpg

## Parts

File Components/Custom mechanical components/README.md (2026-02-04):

Material developed by Steve Smith or members of the Bustamante Group or people employed by UC Berkeley is subject to the following copyright: Copyright (c)2009. The Regents of the University of California (Regents). All Rights Reserved. Permission to use, copy, modify, and distribute these plans and software for educational, research, and not-for-profit purposes, without fee and without a signed licensing agreement, is hereby granted, provided that the above copyright notice, this paragraph and the following two paragraphs appear in all copies, modifications, and distributions. Contact The Office of Technology Licensing, UC Berkeley, 2150 Shattuck Avenue, Suite 510, Berkeley, CA 94720-1620, (510) 643-7201, for commercial licensing opportunities. IN NO EVENT SHALL REGENTS BE LIABLE TO ANY PARTY FOR DIRECT, INDIRECT, SPECIAL, INCIDENTAL, OR CONSEQUENTIAL DAMAGES, INCLUDING LOST PROFITS, ARISING OUT OF THE USE OF THESE PLANS, SOFTWARE OR ITS DOCUMENTATION, EVEN IF REGENTS HAS BEEN ADVISED OF THE POSSIBILITY OF SUCH DAMAGE. REGENTS SPECIFICALLY DISCLAIMS ANY WARRANTIES, INCLUDING, BUT NOT LIMITED TO, THE IMPLIED WARRANTIES OF MERCHANTABILITY AND FITNESS FOR A PARTICULAR PURPOSE. THE PLANS, SOFTWARE AND ACCOMPANYING DOCUMENTATION, IF ANY, PROVIDED HEREUNDER IS PROVIDED "AS IS". REGENTS HAS NO OBLIGATION TO PROVIDE MAINTENANCE, SUPPORT, UPDATES, ENHANCEMENTS, OR MODIFICATIONS.
Material submitted from outside sources should bear the author's copyright notice if applicable. The University of California assumes no liability for the use of contributed material.

For a few components we currently only provide step files, the materials to use for these are:
The material for these are:
  - Chamber Holder Pin - Brass
  - PSD Holder Handle - Alluminum alloy
  - Aperture iris button - Black plastic
  - Filter holder disc - Black plastic

Both the aperture iris button and the filter holder disc can be printed with a 3D printer (print in PLA or ABS dark plastic). Since many prints expand a little it may be necessary to decrease the size a little to get a tight fit.

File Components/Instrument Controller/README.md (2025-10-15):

# Bills of materials for the instrument controller

The boards are connected using two ribbon cable with 34-pin connectors.
Specifically two : 
With the two ... on them.
## Boards

###  Microcontroller board
Hosts the arduino portenta H7 (not included in BOM). Besides this has only two connectors to connect the arduino and two to connect to other boards. The USB port on the arduino is used for communications with the host computer.

### Sensor board
Amplifies the signals from the various photosensors and hosts the analog digital converter used to sample these signals.

### Actuator board
Used to steer the motors of the instrument and to move the lasers.

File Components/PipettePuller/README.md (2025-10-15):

# 3D printable files for the pipette puller

Printing the 3D printable components is possible with most modern 3D printers. The puller has been tested with PLA filament.

Assembling the puller is easy, follow the steps in the PipettePullerAssembly video of this GitHub.

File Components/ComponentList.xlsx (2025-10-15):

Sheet: Tweezers Instrument
Name | Manufacturer | Product ID | Vendor | Number required | Stock | Cost
Cable Clamp (http://tweezerslab.unipr.it/cgi-bin/parts.pl/Show?_id=3da2) | Nylon, 1/4" dia. | 839-7625 | Allied Electronics (http://alliedelec.com/) | 3 |  | $0.07
Cable, 6 cond (http://tweezerslab.unipr.it/cgi-bin/parts.pl/Show?_id=27ba) | Belden 9536 | 216-2813 | Allied Electronics (http://alliedelec.com/) | 24 |  | $0.52
Cable, 9 cond (http://tweezerslab.unipr.it/cgi-bin/parts.pl/Show?_id=87ea) | Belden 9423 | 216-2210 | Allied Electronics (http://alliedelec.com/) | 12 |  | $0.82
Connector header 2 pos RA (http://tweezerslab.unipr.it/cgi-bin/parts.pl/Show?_id=3d83) | Molex 70553-0001 | 863-0787 | Allied Electronics (http://alliedelec.com/) | 1 |  | $0.41
connector housing 2 jack inline (http://tweezerslab.unipr.it/cgi-bin/parts.pl/Show?_id=e30e) | molex 70107-0001 | 70191071 | Allied Electronics (http://alliedelec.com/) | 1 |  | $0.53
Connector housing 4 pos vert friction lock (http://tweezerslab.unipr.it/cgi-bin/parts.pl/Show?_id=b67c) | Molex 22-01-3047 | 863-0253 | Allied Electronics (http://alliedelec.com/) | 2 |  | $0.15
Connector housing, 2 plug (http://tweezerslab.unipr.it/cgi-bin/parts.pl/Show?_id=b0a0) | Molex 50-57-9402 | 863-0476 | Allied Electronics (http://alliedelec.com/) | 1 |  | $0.35
Connector housing, 4 plug (http://tweezerslab.unipr.it/cgi-bin/parts.pl/Show?_id=326a) | Molex 50-57-9404 | 863-0274 | Allied Electronics (http://alliedelec.com/) | 1 |  | $0.19
Resistor, 1/4W, Carbon Film 5% (http://tweezerslab.unipr.it/cgi-bin/parts.pl/Show?_id=11fc) | 220 ohm, Ohmite OK2215E | 296-4751 | Allied Electronics (http://alliedelec.com/) | 1 |  | $0.05
Ribbon cable 16 Cond (http://tweezerslab.unipr.it/cgi-bin/parts.pl/Show?_id=6d05) | alpha 3580/16 | 943-1314 | Allied Electronics (http://alliedelec.com/) | 6 |  | $1.11
Ribbon cable 34 Cond (http://tweezerslab.unipr.it/cgi-bin/parts.pl/Show?_id=2fc7) | alpha 3580/34 | 943-1319 | Allied Electronics (http://alliedelec.com/) | 6 |  | $1.00
screw, lock kit (http://tweezerslab.unipr.it/cgi-bin/parts.pl/Show?_id=83c7) | Cinch D20419-16 | 750-7002 | Allied Electronics (http://alliedelec.com/) | 2 |  | $1.18
Terminal (http://tweezerslab.unipr.it/cgi-bin/parts.pl/Show?_id=f42c) | Vector T49 | 977-5060 | Allied Electronics (http://alliedelec.com/) | 6 |  | $0.16
terminal crimp (http://tweezerslab.unipr.it/cgi-bin/parts.pl/Show?_id=fbcf) | molex 16-02-0117 | 70190984 | Allied Electronics (http://alliedelec.com/) | 2 |  | $0.23
retarder film (http://tweezerslab.unipr.it/cgi-bin/parts.pl/Show?_id=170e) | 1/2 Wave | U27342 | Anchor Optics (http://www.anchoroptics.com/) | 1 |  | $11.05
Digital camera | Basler monochrome | a2A5320-23umBAS | Basler | 1 |  | $2000
syringe (http://tweezerslab.unipr.it/cgi-bin/parts.pl/Show?_id=43a7) | 1 ml, tuberculin | 309602 | Becton Dickinson (http://www.bd.com/) | 3 |  | $0.50
tubing , Polyethylene (http://tweezerslab.unipr.it/cgi-bin/parts.pl/Show?_id=c061) | Intramedic PE 10 | 427401 | Becton Dickinson (http://www.bd.com/) | 2 |  | $1.00
Solenoid pinch valve (http://tweezerslab.unipr.it/cgi-bin/parts.pl/Show?_id=a90e) | Cole Parmer EW-98302-00 | EW-98302-00 | Cole Parmer (http://www.coleparmer.com/) | 1 |  | $73.00
D Ring (http://tweezerslab.unipr.it/cgi-bin/parts.pl/Show?_id=73ee) | 3/8 in | NCD 38-25 | CreativeDesignWorks (http://cdwplus.com/) | 3 |  | $0.12
Key Ring (http://tweezerslab.unipr.it/cgi-bin/parts.pl/Show?_id=6bd6) | 1 1/4 in | KEY NP 125-10 | CreativeDesignWorks (http://cdwplus.com/) | 1 |  | $0.30
Webbing, nylon (http://tweezerslab.unipr.it/cgi-bin/parts.pl/Show?_id=7baa) | 3/8 in wide | WBH 38-50 | CreativeDesignWorks (http://cdwplus.com/) | 4 |  | $0.52
Lens (http://tweezerslab.unipr.it/cgi-bin/parts.pl/Show?_id=dd1d) | achromat, f=175 | PAC061 | Newport Corporation (http://www.newport.com/) | 1 |  | $74.00
Polarizing Cube Beamsplitter (http://tweezerslab.unipr.it/cgi-bin/parts.pl/Show?_id=b905) | PBS-810-050 |  | CVI/Melles Griot (http://www.cvimellesgriot.com/) | 4 |  | $220.00
Cable Clamp (http://tweezerslab.unipr.it/cgi-bin/parts.pl/Show?_id=6b30) | Nylon, 3/8" dia. | 7629K-ND | DigiKey (http://www.digikey.com/) | 2 |  | $0.06
Cable Clamp (http://tweezerslab.unipr.it/cgi-bin/parts.pl/Show?_id=9a30) | Nylon, 3/16" dia. | 7623K-ND | DigiKey (http://www.digikey.com/) | 2 |  | $0.05
Cable tie (http://tweezerslab.unipr.it/cgi-bin/parts.pl/Show?_id=9bfe) | Panduit Corp PLT1.5M-C | 298-1024-ND | DigiKey (http://www.digikey.com/) | 2 |  | $0.20
Connector header 4 pos RA (http://tweezerslab.unipr.it/cgi-bin/parts.pl/Show?_id=5001) | Molex 70553-0003 | WM4902-ND | DigiKey (http://www.digikey.com/) | 1 |  | $0.93
Connector header 4 pos vert friction-lock (http://tweezerslab.unipr.it/cgi-bin/parts.pl/Show?_id=b489) | Molex 22-29-2041 | WM2746-ND | DigiKey (http://www.digikey.com/) | 2 |  | $1.09
Connector, 8 pos double-row plug (http://tweezerslab.unipr.it/cgi-bin/parts.pl/Show?_id=d7da) | Molex 22-55-2081 | 863-0793 | DigiKey (http://www.digikey.com/) | 4 |  | $0.83
Connector, plug ribbon 10 (http://tweezerslab.unipr.it/cgi-bin/parts.pl/Show?_id=328c) | 3M 4610-6050 | MPL10K-ND | DigiKey (http://www.digikey.com/) | 3 |  | $2.95
Diode, Schottky (http://tweezerslab.unipr.it/cgi-bin/parts.pl/Show?_id=8656) | 1N5818 | 1N5818FSCT-ND | DigiKey (http://www.digikey.com/) | 2 |  | $0.54
pinch clamp motor (http://tweezerslab.unipr.it/cgi-bin/parts.pl/Show?_id=a74f) | Cramer 30569 | CRA202-ND | DigiKey (http://www.digikey.com/) | 1 |  | $38.64
Filter ND absorption (http://tweezerslab.unipr.it/cgi-bin/parts.pl/Show?_id=a592) | NT48-532 | NT48-532 | Edmund Optics (http://www.edmundoptics.com/) | 3 |  | $22.00
Filter ND REF 12.5 DIA 0.5OD (http://tweezerslab.unipr.it/cgi-bin/parts.pl/Show?_id=16a6) | NT46-132 | NT46-132 | Edmund Optics (http://www.edmundoptics.com/) | 2 |  | $25.00
Hybrid beamsplitter (http://tweezerslab.unipr.it/cgi-bin/parts.pl/Show?_id=9f0d) | NT49-005 | NT49-005 | Edmund Optics (http://www.edmundoptics.com/) | 2 |  | $175.00
Mirror (http://tweezerslab.unipr.it/cgi-bin/parts.pl/Show?_id=aa33) | NT43-880 | NT43-880 | Edmund Optics (http://www.edmundoptics.com/) | 6 |  | $38.00
Buffer bottle, pressure (http://tweezerslab.unipr.it/cgi-bin/parts.pl/Show?_id=03f1) | custom shop |  | glass blowing shop (http://tweezerslab.unipr.it/cgi-bin/vendors.pl/Show?_id=eda7) | 1 |  | $50.00
brass tube 1/32" (http://tweezerslab.unipr.it/cgi-bin/parts.pl/Show?_id=f67e) | Special Shapes | 96017-12 | K and S Engineering (http://www.ksmetals.com/) | 0.02 |  | $1.25
tube, rectangular brass 5/32 x 5/16"" (http://tweezerslab.unipr.it/cgi-bin/parts.pl/Show?_id=2118) | K and S Engineering | 95031 | K and S Engineering (http://www.ksmetals.com/) | 0.02 |  | $3.39
tube, round 3/32" (http://tweezerslab.unipr.it/cgi-bin/parts.pl/Show?_id=5ddf) | K and S Engineering | 97021 | K and S Engineering (http://www.ksmetals.com/) | 1 |  | $0.75
tube, square brass 3/16" (http://tweezerslab.unipr.it/cgi-bin/parts.pl/Show?_id=420c) | K and S Engineering | 92050 | K and S Engineering (http://www.ksmetals.com/) | 1 |  | $1.69
tube, square brass 5/32" (http://tweezerslab.unipr.it/cgi-bin/parts.pl/Show?_id=356b) | K and S Engineering | 92040 | K and S Engineering (http://www.ksmetals.com/) | 1 |  | $1.59
Parafilm (http://tweezerslab.unipr.it/cgi-bin/parts.pl/Show?_id=ff58) | Parafilm,4inx250ft | P7668 | SigmaAldrich (http://www.karlan.com/) | 0.001 |  | $20.00
Glass tubing - dispenser type (http://tweezerslab.unipr.it/cgi-bin/parts.pl/Show?_id=004f) | Garner Glass | ID = 25um (tol. +/-6.4um), OD=100um (tol. +/-6.4um), Length = 150mm | King Precision Glass (http://www.kingprecisionglass.com/) | 0.2 |  | $2.00
glass tubing for pipette (http://tweezerslab.unipr.it/cgi-bin/parts.pl/Show?_id=f8c7) | King Precision Glass (formerly Garner Glass) | KG-33 or 7740) ID= 40um (tol. +/-6.4um), OD = 80um (tol. +/-6.4um), Length =150mm | King Precision Glass (http://www.kingprecisionglass.com/) | 0.5 |  | $1.00
tubing, Teflon (http://tweezerslab.unipr.it/cgi-bin/parts.pl/Show?_id=f85a) | #24 thin wall | ZEULW-24-C | Lapp Tannehill (http://www.lapptannehill.com/) | 3 |  | $0.21
Laser (http://tweezerslab.unipr.it/cgi-bin/parts.pl/Show?_id=0605) | LU0808M250-FBG | LU0808M250-FBG | Lumics GmbH (http://www.lumics.com/) | 2 |  | $1800.00
Knob (http://tweezerslab.unipr.it/cgi-bin/parts.pl/Show?_id=5546) | for #6 capScrew | 94052A023 | McMaster Carr (http://www.mcmaster.com/) | 4 |  | $0.12
Knob (http://tweezerslab.unipr.it/cgi-bin/parts.pl/Show?_id=3c2e) | for #4 capScrew | 94052A121 | McMaster Carr (http://www.mcmaster.com/) | 12 |  | $0.12
Screw, SS Allen Cap (http://tweezerslab.unipr.it/cgi-bin/parts.pl/Show?_id=a06d) | 2-56 x 3/16 | 92196A076 | McMaster Carr (http://www.mcmaster.com/) | 8 |  | $0.06
Screw, SS Allen-cap (http://tweezerslab.unipr.it/cgi-bin/parts.pl/Show?_id=b826) | 8-32x1 | 92196A199 | McMaster Carr (http://www.mcmaster.com/) | 8 |  | $0.09
Screw, SS Allen-cap (http://tweezerslab.unipr.it/cgi-bin/parts.pl/Show?_id=4e40) | 8-32x3/8 | 92196A192 | McMaster Carr (http://www.mcmaster.com/) | 2 |  | $0.06
Screw, SS Allen-cap (http://tweezerslab.unipr.it/cgi-bin/parts.pl/Show?_id=6080) | 8-32x5/8 | 92196A196 | McMaster Carr (http://www.mcmaster.com/) | 6 |  | $0.07
Screw, SS Allen-cap (http://tweezerslab.unipr.it/cgi-bin/parts.pl/Show?_id=fa21) | 6-32x7/8 | 92196A152 | McMaster Carr (http://www.mcmaster.com/) | 16 |  | $0.07
Screw, SS Allen-cap (http://tweezerslab.unipr.it/cgi-bin/parts.pl/Show?_id=80fe) | 6-32x3/8 | 92196A146 | McMaster Carr (http://www.mcmaster.com/) | 12 |  | $0.06
Screw, SS Allen-cap (http://tweezerslab.unipr.it/cgi-bin/parts.pl/Show?_id=b61a) | 4-40x3/16 | 92196A105 | McMaster Carr (http://www.mcmaster.com/) | 28 |  | $0.12
Screw, SS Allen-cap (http://tweezerslab.unipr.it/cgi-bin/parts.pl/Show?_id=e5d1) | 4-40x1/2 | 92196A110 | McMaster Carr (http://www.mcmaster.com/) | 23 |  | $0.05
Screw, SS Allen-cap (http://tweezerslab.unipr.it/cgi-bin/parts.pl/Show?_id=e3b2) | 2-56x1/2 | 92196A081 | McMaster Carr (http://www.mcmaster.com/) | 4 |  | $0.07
Screw, SS Allen-cap (http://tweezerslab.unipr.it/cgi-bin/parts.pl/Show?_id=98e9) | 4-40x3/8 | 92196A108 | McMaster Carr (http://www.mcmaster.com/) | 5 |  | $0.04
Screw, SS Allen-cap (http://tweezerslab.unipr.it/cgi-bin/parts.pl/Show?_id=c8f3) | 8-32x3/4 | 92196A197 | McMaster Carr (http://www.mcmaster.com/) | 22 |  | $0.08
Screw, SS Allen-cap (http://tweezerslab.unipr.it/cgi-bin/parts.pl/Show?_id=97ca) | 8-32x7/8 | 92195A198 | McMaster Carr (http://www.mcmaster.com/) | 4 |  | $0.09
Screw, SS Flat Head (http://tweezerslab.unipr.it/cgi-bin/parts.pl/Show?_id=e54f) | 6-32x1/2 | 91771A148 | McMaster Carr (http://www.mcmaster.com/) | 13 |  | $0.05
Screw, SS Flat Head (http://tweezerslab.unipr.it/cgi-bin/parts.pl/Show?_id=6163) | 6-32x1/4 | 91771A144 | McMaster Carr (http://www.mcmaster.com/) | 3 |  | $0.06
Screw, SS Flat-head (http://tweezerslab.unipr.it/cgi-bin/parts.pl/Show?_id=7a2f) | 2-56x3/16 | 91771A076 | McMaster Carr (http://www.mcmaster.com/) | 36 |  | $0.06
Screw, SS Flat-Head (http://tweezerslab.unipr.it/cgi-bin/parts.pl/Show?_id=5fe1) | 2-56 x 3/4" | 91771A084 | McMaster Carr (http://www.mcmaster.com/) | 2 |  | $0.05
Screw, SS Flat-Head (http://tweezerslab.unipr.it/cgi-bin/parts.pl/Show?_id=bae5) | 4-40x1/2 | 91771A110 | McMaster Carr (http://www.mcmaster.com/) | 18 |  | $0.04
Screw, SS set (http://tweezerslab.unipr.it/cgi-bin/parts.pl/Show?_id=e51e) | 8-32 x 1.25" | 92311A201 | McMaster Carr (http://www.mcmaster.com/) | 6 |  | $0.26
Screw, SS set (http://tweezerslab.unipr.it/cgi-bin/parts.pl/Show?_id=1fbd) | 2-56x3/32 | 92311A073 | McMaster Carr (http://www.mcmaster.com/) | 6 |  | $0.13
Spacer, Brass (http://tweezerslab.unipr.it/cgi-bin/parts.pl/Show?_id=3f2a) | 1/4" dia., 6-32 threading, 3/4" length | 92474A447 | McMaster Carr (http://www.mcmaster.com/) | 5 |  | $0.82
Spacer, Brass (http://tweezerslab.unipr.it/cgi-bin/parts.pl/Show?_id=cee0) | 1/4" long, 1/4" o.d., .115" i.d., non-threaded | 90309A219 | McMaster Carr (http://www.mcmaster.com/) | 4 |  | $0.30
Super glue (http://tweezerslab.unipr.it/cgi-bin/parts.pl/Show?_id=a843) | Loctite Super Bonder® 495™ | 7478A11 | McMaster Carr (http://www.mcmaster.com/) | 0.04 |  | $3.60
Washer (http://tweezerslab.unipr.it/cgi-bin/parts.pl/Show?_id=42cf) | SS #8 | 98017A624 | McMaster Carr (http://www.mcmaster.com/) | 3 |  | $0.07
Connector hood DB9 (http://tweezerslab.unipr.it/cgi-bin/parts.pl/Show?_id=0d7c) | Cinch DE-24657-30 | 538-DE-24657-30 | Mouser Electronics (http://www.mouser.com/home.aspx) | 2 |  | $4.26
LED blue 3mm (http://tweezerslab.unipr.it/cgi-bin/parts.pl/Show?_id=d644) | VCC Electronics VAOL-3GSBY4 |  | Mouser Electronics (http://www.mouser.com/home.aspx) | 1 |  | $0.47
Ribbon Socket, 16 (http://tweezerslab.unipr.it/cgi-bin/parts.pl/Show?_id=e611) | AMP-Tyco 1658622-3 | 571-1658622-3 | Mouser Electronics (http://www.mouser.com/home.aspx) | 1 |  | $1.48
Ribbon Socket, 34 (http://tweezerslab.unipr.it/cgi-bin/parts.pl/Show?_id=534a) | AMP-Tyco 1658622-8 | 571-1658622-8 | Mouser Electronics (http://www.mouser.com/home.aspx) | 1 |  | $3.58
Connector, DE-9P (http://tweezerslab.unipr.it/cgi-bin/parts.pl/Show?_id=cb43) | Cinch DE-9P | 43F200 | Newark (http://www.newark.com/) | 2 |  | $2.83
Temp Sensor (http://tweezerslab.unipr.it/cgi-bin/parts.pl/Show?_id=bdd7) | AD590JH | ADJ590JH | Newark (http://www.newark.com/) | 2 |  | $7.80
Terminal, crimp (http://tweezerslab.unipr.it/cgi-bin/parts.pl/Show?_id=d62b) | Molex 16-02-0104 | 16-02-0104 | Newark (http://www.newark.com/) | 34 |  | $0.12
Lens (http://tweezerslab.unipr.it/cgi-bin/parts.pl/Show?_id=9372) | plano-convex, f=75 | KPX055 | Newport Corporation (http://www.newport.com/) | 2 |  | $35.00
Lens (http://tweezerslab.unipr.it/cgi-bin/parts.pl/Show?_id=7cb3) | plano-convex, f=63 | KPX052 | Newport Corporation (http://www.newport.com/) | 2 |  | $35.00
Lens (http://tweezerslab.unipr.it/cgi-bin/parts.pl/Show?_id=d750) | bi-convex, f = 50 | KBX034 | Newport Corporation (http://www.newport.com/) | 1 |  | $30.00
Objective slider (http://tweezerslab.unipr.it/cgi-bin/parts.pl/Show?_id=a500) | DS40-X | DS40-X | Newport Corporation (http://www.newport.com/) | 1 |  | $130.00
Prism, RA (http://tweezerslab.unipr.it/cgi-bin/parts.pl/Show?_id=c8f9) | 05BR08 | 05BR08 | Newport Corporation (http://www.newport.com/) | 4 |  | $69.00
Retro reflector (http://tweezerslab.unipr.it/cgi-bin/parts.pl/Show?_id=0313) | Newport BGR-6.35 | BGR-6.35 | Newport Corporation (http://www.newport.com/) | 1 |  | $379.00
XYZ Stage (http://tweezerslab.unipr.it/cgi-bin/parts.pl/Show?_id=4679) | 561D-XYZ | 561D-XYZ | Newport Corporation (http://www.newport.com/) | 1 |  | $1734.00
Objective lens (http://tweezerslab.unipr.it/cgi-bin/parts.pl/Show?_id=4b41) | UPLSAPO 60XW | UPLSAPO 60XW | Olympus America (http://www.olympusamerica.com/seg_section/uis2/seg_uis2.asp) | 2 |  | $7430.00
Photo-diode (http://tweezerslab.unipr.it/cgi-bin/parts.pl/Show?_id=8e83) | PIN-10DI | PIN-10DI | OSI Optoelectronics (http://www.udt.com/) | 2 |  | $50.00
PSD large (http://tweezerslab.unipr.it/cgi-bin/parts.pl/Show?_id=9bec) | DL-10 | PIN DL-10 | OSI Optoelectronics (http://www.udt.com/) | 2 |  | $195.00
PSD small (http://tweezerslab.unipr.it/cgi-bin/parts.pl/Show?_id=9064) | DL-4 | PIN DL-4 | OSI Optoelectronics (http://www.udt.com/) | 2 |  | $75.00
screw, Nylon set (http://tweezerslab.unipr.it/cgi-bin/parts.pl/Show?_id=0e30) | 8-32 x 3/8" | S27-077 | Product-Components (http://www.product-components.com/) | 6 |  | $0.25
tubing , silicone rubber , Tygon 3350 (http://tweezerslab.unipr.it/cgi-bin/parts.pl/Show?_id=9b0b) | Saint-Gobain, ID 1/32", OD 3/32" | Tygon 3350 | Professional Plastics (http://www.professionalplastics.com/) | 6 |  | $0.11
Magnet (http://tweezerslab.unipr.it/cgi-bin/parts.pl/Show?_id=bb94) | Radio Shack |  | Radio Shack (http://www.radioshack.com/) | 3 |  | $1.99
brass tube (http://tweezerslab.unipr.it/cgi-bin/parts.pl/Show?_id=8209) | 1/16" | TTRB-01-12-03 | Small Parts Inc. (http://www.smallparts.com/) | 0.2 |  | $2.71
brass tube (http://tweezerslab.unipr.it/cgi-bin/parts.pl/Show?_id=dd7d) | 5/32" | TTRB-04-12-03 | Small Parts Inc. (http://www.smallparts.com/) | 0.2 |  | $4.41
brass tube (http://tweezerslab.unipr.it/cgi-bin/parts.pl/Show?_id=f9b9) | 1/8" | TTRB-03-12-03 | Small Parts Inc. (http://www.smallparts.com/) | 0.2 |  | $3.67
brass tube (http://tweezerslab.unipr.it/cgi-bin/parts.pl/Show?_id=67a0) | 3/32" | TTRB-02-12-03 | Small Parts Inc. (http://www.smallparts.com/) | 0.2 |  | $2.81
Cable, Stainless (http://tweezerslab.unipr.it/cgi-bin/parts.pl/Show?_id=0f15) | 1/32" diameter | B-MCXU-1/32-100ft | Small Parts Inc. (http://www.smallparts.com/) | 6 |  | $0.25
needle , hypodermic (http://tweezerslab.unipr.it/cgi-bin/parts.pl/Show?_id=ccf3) | #23 blunt tip | B0013J1V3W | Small Parts Inc. (http://www.smallparts.com/) | 2 |  | $0.38
needle , hypodermic (http://tweezerslab.unipr.it/cgi-bin/parts.pl/Show?_id=e442) | #30 blunt tip | B0013IZT8Q | Small Parts Inc. (http://www.smallparts.com/) | 1 |  | $0.29
tubing , Stainless (http://tweezerslab.unipr.it/cgi-bin/parts.pl/Show?_id=fafc) | #17 hypodermic | HTX-17R-12-05 | Small Parts Inc. (http://www.smallparts.com/) | 0.5 |  | $2.00
tubing, Teflon (http://tweezerslab.unipr.it/cgi-bin/parts.pl/Show?_id=c0ee) | #18 Thin Wall | TWTT-18-50ft | Small Parts Inc. (http://www.smallparts.com/) | 6 |  | $0.50
Pivot Screen (http://tweezerslab.unipr.it/cgi-bin/parts.pl/Show?_id=8431) | Ted Pella | 1GC150 | Ted Pella Inc. (http://www.tedpella.com/) | 2 |  | $0.20
Actuator motor OBSOLETE (http://tweezerslab.unipr.it/cgi-bin/parts.pl/Show?_id=c65f) | Thorlabs Z606 | Thorlabs Z606, working on electronics for updated z906 | Thorlabs (http://www.thorlabs.com/) | 3 |  | $320.00
Adhesive, Optical (http://tweezerslab.unipr.it/cgi-bin/parts.pl/Show?_id=31f0) | Norland | NOA601 | Thorlabs (http://www.thorlabs.com/) | 0.002 |  | $27.60
Adj. Screw (http://tweezerslab.unipr.it/cgi-bin/parts.pl/Show?_id=98ae) | Thorlabs | F19SS100 | Thorlabs (http://www.thorlabs.com/) | 6 |  | $9.50
Fiber adapter (http://tweezerslab.unipr.it/cgi-bin/parts.pl/Show?_id=7179) | ADAFC2 | ADAFC2 | Thorlabs (http://www.thorlabs.com/) | 2 |  | $10.20
Fiber Optic Connector (http://tweezerslab.unipr.it/cgi-bin/parts.pl/Show?_id=6127) | Thorlabs | 30125D2 | Thorlabs (http://www.thorlabs.com/) | 2 |  | $12.00
Filter (http://tweezerslab.unipr.it/cgi-bin/parts.pl/Show?_id=adbe) | blue glass | FGB37S | Thorlabs (http://www.thorlabs.com/) | 0.6 |  | $82.00
Lens (http://tweezerslab.unipr.it/cgi-bin/parts.pl/Show?_id=b24b) | plastic, f=12mm | CSX122 | Thorlabs (http://www.thorlabs.com/) | 2 |  | $12.00
Lens (http://tweezerslab.unipr.it/cgi-bin/parts.pl/Show?_id=f58b) | achromat, f=20mm | AC080-020-B | Thorlabs (http://www.thorlabs.com/) | 2 |  | $38.00
Mirror mount 2-screw (http://tweezerslab.unipr.it/cgi-bin/parts.pl/Show?_id=0e69) | KM05 | KM05 | Thorlabs (http://www.thorlabs.com/) | 2 |  | $42.00
Mirror mount 3-screw (http://tweezerslab.unipr.it/cgi-bin/parts.pl/Show?_id=e9cb) | KS05 | KS05 | Thorlabs (http://www.thorlabs.com/) | 2 |  | $66.00
Optical fiber (http://tweezerslab.unipr.it/cgi-bin/parts.pl/Show?_id=fcc6) | Fibercore | SM800-5.6-125 | Thorlabs (http://www.thorlabs.com/) | 0.6 |  | $5.40
Pellicle (http://tweezerslab.unipr.it/cgi-bin/parts.pl/Show?_id=7f48) | BP108 | BP108 | Thorlabs (http://www.thorlabs.com/) | 2 |  | $77.70
Piezo stack (http://tweezerslab.unipr.it/cgi-bin/parts.pl/Show?_id=d47d) | Co-fired piezo actuator | PC4WM | Thorlabs (http://www.thorlabs.com/) | 4 |  | $79.80
pinch clamp nut (http://tweezerslab.unipr.it/cgi-bin/parts.pl/Show?_id=93ee) | Thorlabs | N100L5P | Thorlabs (http://www.thorlabs.com/) | 1 |  | $10.70
pinch clamp screw (http://tweezerslab.unipr.it/cgi-bin/parts.pl/Show?_id=d2e5) | Thorlabs | UFS100 | Thorlabs (http://www.thorlabs.com/) | 1 |  | $14.70
Retainer rings (http://tweezerslab.unipr.it/cgi-bin/parts.pl/Show?_id=9f62) | SM05RR | SM05RR | Thorlabs (http://www.thorlabs.com/) | 16 |  | $5.10
Tape (http://tweezerslab.unipr.it/cgi-bin/parts.pl/Show?_id=ece9) | black 1" x 60 yds. | T137-1.0 | Thorlabs (http://www.thorlabs.com/) | 1 |  | $7.87
tubing, furcation (http://tweezerslab.unipr.it/cgi-bin/parts.pl/Show?_id=6e4b) | fiber optic | FT900SM | Thorlabs (http://www.thorlabs.com/) | 0.4 |  | $2.00
Waveplate (http://tweezerslab.unipr.it/cgi-bin/parts.pl/Show?_id=0ff2) | WPQ05M-808 | WPQ05M-808 | Thorlabs (http://www.thorlabs.com/) | 2 |  | $410.00
PC board (http://tweezerslab.unipr.it/cgi-bin/parts.pl/Show?_id=7c7c) | Laser_Diode_Mount @10 |  | Various board manufacturers (http://tweezerslab.unipr.it/cgi-bin/vendors.pl/Show?_id=e1a2) | 2 |  | $13.12
PC Board (http://tweezerslab.unipr.it/cgi-bin/parts.pl/Show?_id=6ffe) | Detectors @4 boards |  | Various board manufacturers (http://tweezerslab.unipr.it/cgi-bin/vendors.pl/Show?_id=e1a2) | 1 |  | $59.50
Beam block nut (http://tweezerslab.unipr.it/cgi-bin/parts.pl/Show?_id=3c8f) | custom shop |  | Various machine shops (http://tweezerslab.unipr.it/cgi-bin/vendors.pl/Show?_id=fd96) | 2 |  | $10.00
Bottle clip (http://tweezerslab.unipr.it/cgi-bin/parts.pl/Show?_id=d4e1) | custom shop |  | Various machine shops (http://tweezerslab.unipr.it/cgi-bin/vendors.pl/Show?_id=fd96) | 2 |  | $15.00
bottle stand (http://tweezerslab.unipr.it/cgi-bin/parts.pl/Show?_id=8724) | custom shop |  | Various machine shops (http://tweezerslab.unipr.it/cgi-bin/vendors.pl/Show?_id=fd96) | 2 |  | $45.00
Bullseye filter, 8 mm (http://tweezerslab.unipr.it/cgi-bin/parts.pl/Show?_id=c5c0) | custom shop |  | Various machine shops (http://tweezerslab.unipr.it/cgi-bin/vendors.pl/Show?_id=fd96) | 2 |  | $20.00
chamber clamp long (http://tweezerslab.unipr.it/cgi-bin/parts.pl/Show?_id=d7d8) | custom shop |  | Various machine shops (http://tweezerslab.unipr.it/cgi-bin/vendors.pl/Show?_id=fd96) | 2 |  | $25.00
chamber clamp short (http://tweezerslab.unipr.it/cgi-bin/parts.pl/Show?_id=4654) | custom shop |  | Various machine shops (http://tweezerslab.unipr.it/cgi-bin/vendors.pl/Show?_id=fd96) | 1 |  | $25.00
chamber holder frame (http://tweezerslab.unipr.it/cgi-bin/parts.pl/Show?_id=636a) | custom shop |  | Various machine shops (http://tweezerslab.unipr.it/cgi-bin/vendors.pl/Show?_id=fd96) | 1 |  | $130.00
Chamber holder pin (http://tweezerslab.unipr.it/cgi-bin/parts.pl/Show?_id=f301) | custom shop |  | Various machine shops (http://tweezerslab.unipr.it/cgi-bin/vendors.pl/Show?_id=fd96) | 2 |  | $10.00
chamber leg (http://tweezerslab.unipr.it/cgi-bin/parts.pl/Show?_id=ad7f) | custom shop |  | Various machine shops (http://tweezerslab.unipr.it/cgi-bin/vendors.pl/Show?_id=fd96) | 2 |  | $55.00
crossbar bracket (http://tweezerslab.unipr.it/cgi-bin/parts.pl/Show?_id=434d) | custom shop |  | Various machine shops (http://tweezerslab.unipr.it/cgi-bin/vendors.pl/Show?_id=fd96) | 4 |  | $40.00
crossbar slider (http://tweezerslab.unipr.it/cgi-bin/parts.pl/Show?_id=b20b) | custom shop |  | Various machine shops (http://tweezerslab.unipr.it/cgi-bin/vendors.pl/Show?_id=fd96) | 2 |  | $45.00
detector cross bar (http://tweezerslab.unipr.it/cgi-bin/parts.pl/Show?_id=228b) | custom shop |  | Various machine shops (http://tweezerslab.unipr.it/cgi-bin/vendors.pl/Show?_id=fd96) | 2 |  | $50.00
DL-2 base (http://tweezerslab.unipr.it/cgi-bin/parts.pl/Show?_id=359e) | custom shop |  | Various machine shops (http://tweezerslab.unipr.it/cgi-bin/vendors.pl/Show?_id=fd96) | 2 |  | $50.00
DL-2 holder (http://tweezerslab.unipr.it/cgi-bin/parts.pl/Show?_id=3744) | custom shop |  | Various machine shops (http://tweezerslab.unipr.it/cgi-bin/vendors.pl/Show?_id=fd96) | 2 |  | $50.00
Fiber Feedthru Plate (http://tweezerslab.unipr.it/cgi-bin/parts.pl/Show?_id=e777) | custom shop |  | Various machine shops (http://tweezerslab.unipr.it/cgi-bin/vendors.pl/Show?_id=fd96) | 2 |  | $20.00
field lens washer (http://tweezerslab.unipr.it/cgi-bin/parts.pl/Show?_id=b5b6) | custom shop |  | Various machine shops (http://tweezerslab.unipr.it/cgi-bin/vendors.pl/Show?_id=fd96) | 1 |  | $30.00
Filter flipper (http://tweezerslab.unipr.it/cgi-bin/parts.pl/Show?_id=3ba7) | custom shop |  | Various machine shops (http://tweezerslab.unipr.it/cgi-bin/vendors.pl/Show?_id=fd96) | 2 |  | $15.00
filter holder disc (http://tweezerslab.unipr.it/cgi-bin/parts.pl/Show?_id=7062) | custom shop |  | Various machine shops (http://tweezerslab.unipr.it/cgi-bin/vendors.pl/Show?_id=fd96) | 2 |  | $10.00
Filter Slider Base (http://tweezerslab.unipr.it/cgi-bin/parts.pl/Show?_id=e3c1) | custom shop |  | Various machine shops (http://tweezerslab.unipr.it/cgi-bin/vendors.pl/Show?_id=fd96) | 1 |  | $30.00
Filter Slider Pieces Set (http://tweezerslab.unipr.it/cgi-bin/parts.pl/Show?_id=5af9) | custom shop |  | Various machine shops (http://tweezerslab.unipr.it/cgi-bin/vendors.pl/Show?_id=fd96) | 1 |  | $100.00
fluidics leg (http://tweezerslab.unipr.it/cgi-bin/parts.pl/Show?_id=a697) | custom shop |  | Various machine shops (http://tweezerslab.unipr.it/cgi-bin/vendors.pl/Show?_id=fd96) | 3 |  | $30.00
focus tube (http://tweezerslab.unipr.it/cgi-bin/parts.pl/Show?_id=8deb) | custom shop |  | Various machine shops (http://tweezerslab.unipr.it/cgi-bin/vendors.pl/Show?_id=fd96) | 1 |  | $80.00
focus-tube end cap (http://tweezerslab.unipr.it/cgi-bin/parts.pl/Show?_id=7d94) | custom shop |  | Various machine shops (http://tweezerslab.unipr.it/cgi-bin/vendors.pl/Show?_id=fd96) | 1 |  | $30.00
hex spacer with clip holes (http://tweezerslab.unipr.it/cgi-bin/parts.pl/Show?_id=db29) | custom shop |  | Various machine shops (http://tweezerslab.unipr.it/cgi-bin/vendors.pl/Show?_id=fd96) | 1 |  | $50.00
hex spacers (http://tweezerslab.unipr.it/cgi-bin/parts.pl/Show?_id=8f90) | custom shop |  | Various machine shops (http://tweezerslab.unipr.it/cgi-bin/vendors.pl/Show?_id=fd96) | 5 |  | $45.00
Hexagon Base 6 (http://tweezerslab.unipr.it/cgi-bin/parts.pl/Show?_id=6907) | custom shop |  | Various machine shops (http://tweezerslab.unipr.it/cgi-bin/vendors.pl/Show?_id=fd96) | 1 |  | $250.00
hexagon fluidic base 3 (http://tweezerslab.unipr.it/cgi-bin/parts.pl/Show?_id=6ecf) | custom shop |  | Various machine shops (http://tweezerslab.unipr.it/cgi-bin/vendors.pl/Show?_id=fd96) | 1 |  | $100.00
hexagon top (http://tweezerslab.unipr.it/cgi-bin/parts.pl/Show?_id=14ea) | custom shop |  | Various machine shops (http://tweezerslab.unipr.it/cgi-bin/vendors.pl/Show?_id=fd96) | 1 |  | $250.00
kinematic riser block (http://tweezerslab.unipr.it/cgi-bin/parts.pl/Show?_id=3cfe) | custom shop |  | Various machine shops (http://tweezerslab.unipr.it/cgi-bin/vendors.pl/Show?_id=fd96) | 2 |  | $65.00
kinetic mount bracket (http://tweezerslab.unipr.it/cgi-bin/parts.pl/Show?_id=b09e) | custom shop |  | Various machine shops (http://tweezerslab.unipr.it/cgi-bin/vendors.pl/Show?_id=fd96) | 2 |  | $33.00
laser base (http://tweezerslab.unipr.it/cgi-bin/parts.pl/Show?_id=d6c3) | custom shop |  | Various machine shops (http://tweezerslab.unipr.it/cgi-bin/vendors.pl/Show?_id=fd96) | 2 |  | $250.00
Laser Base Cover (http://tweezerslab.unipr.it/cgi-bin/parts.pl/Show?_id=6ab9) | custom shop |  | Various machine shops (http://tweezerslab.unipr.it/cgi-bin/vendors.pl/Show?_id=fd96) | 2 |  | $33.00
laser cable clamp (http://tweezerslab.unipr.it/cgi-bin/parts.pl/Show?_id=9a9b) | custom shop |  | Various machine shops (http://tweezerslab.unipr.it/cgi-bin/vendors.pl/Show?_id=fd96) | 2 |  | $20.00
LED lamp post (http://tweezerslab.unipr.it/cgi-bin/parts.pl/Show?_id=58fe) | custom shop |  | Various machine shops (http://tweezerslab.unipr.it/cgi-bin/vendors.pl/Show?_id=fd96) | 1 |  | $65.00
LED slider mount (http://tweezerslab.unipr.it/cgi-bin/parts.pl/Show?_id=2b12) | custom shop |  | Various machine shops (http://tweezerslab.unipr.it/cgi-bin/vendors.pl/Show?_id=fd96) | 1 |  | $30.00
left handed stage gizmo (http://tweezerslab.unipr.it/cgi-bin/parts.pl/Show?_id=c1dc) | custom shop |  | Various machine shops (http://tweezerslab.unipr.it/cgi-bin/vendors.pl/Show?_id=fd96) | 1 |  | $150.00
Lens adapter 8mm (http://tweezerslab.unipr.it/cgi-bin/parts.pl/Show?_id=d14c) | custom shop |  | Various machine shops (http://tweezerslab.unipr.it/cgi-bin/vendors.pl/Show?_id=fd96) | 2 |  | $10.00
Light Lever Lens Slider (http://tweezerslab.unipr.it/cgi-bin/parts.pl/Show?_id=c304) | custom shop |  | Various machine shops (http://tweezerslab.unipr.it/cgi-bin/vendors.pl/Show?_id=fd96) | 2 |  | $65.00
light lever mirror bracket (http://tweezerslab.unipr.it/cgi-bin/parts.pl/Show?_id=58f0) | custom shop |  | Various machine shops (http://tweezerslab.unipr.it/cgi-bin/vendors.pl/Show?_id=fd96) | 2 |  | $75.00
light lever mirror riser (http://tweezerslab.unipr.it/cgi-bin/parts.pl/Show?_id=d30e) | custom shop |  | Various machine shops (http://tweezerslab.unipr.it/cgi-bin/vendors.pl/Show?_id=fd96) | 2 |  | $65.00
light lever pickoff tube (http://tweezerslab.unipr.it/cgi-bin/parts.pl/Show?_id=2be4) | custom shop |  | Various machine shops (http://tweezerslab.unipr.it/cgi-bin/vendors.pl/Show?_id=fd96) | 2 |  | $50.00
Light lever standoff spacer (http://tweezerslab.unipr.it/cgi-bin/parts.pl/Show?_id=d280) | custom shop |  | Various machine shops (http://tweezerslab.unipr.it/cgi-bin/vendors.pl/Show?_id=fd96) | 2 |  | $100.00
mirror offset riser (http://tweezerslab.unipr.it/cgi-bin/parts.pl/Show?_id=c210) | custom shop |  | Various machine shops (http://tweezerslab.unipr.it/cgi-bin/vendors.pl/Show?_id=fd96) | 2 |  | $30.00
motor clamp (http://tweezerslab.unipr.it/cgi-bin/parts.pl/Show?_id=321f) | custom shop |  | Various machine shops (http://tweezerslab.unipr.it/cgi-bin/vendors.pl/Show?_id=fd96) | 2 |  | $66.00
Motor Split Bushing (http://tweezerslab.unipr.it/cgi-bin/parts.pl/Show?_id=4df4) | custom shop |  | Various machine shops (http://tweezerslab.unipr.it/cgi-bin/vendors.pl/Show?_id=fd96) | 1 |  | $15.00
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

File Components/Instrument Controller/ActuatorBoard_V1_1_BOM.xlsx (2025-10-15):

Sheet: BOM
0 | 1 | 2 | 3 | 4 | 5 | 6 | 7 | 8 | 9 | 10 | 11 | 12 | 13 | 14 | 15 | 16 | 17 | 18 | 19 | 20 | 21
Qty | Value | Device | Footprint Name | Parts | Detailed Description | ARROW_PART_NUMBER | ARROW_PRICE-STOCK | DESCRIPTION | HEIGHT | MANUFACTURER_NAME | MANUFACTURER_PART_NUMBER | MF | MOUSER_PART_NUMBER | MOUSER_PRICE-STOCK | MOUSER_TESTING_PART_NUMBER | MOUSER_TESTING_PRICE-STOCK | MPN | OC_FARNELL | OC_NEWARK | POPULARITY | SPICEPREFIX
1 |  | 16H | 16H | PIEZO_CONNECTOR | CONNECTOR |  |  |  |  |  |  |  |  |  |  |  |  | unknown | unknown
2 |  | 34H | 34H | MOTOR_CABLE_CONNECTOR, TO_COMPUTEBOARD | CONNECTOR |  |  |  |  |  |  |  |  |  |  |  |  | unknown | unknown
1 |  | L03P | L03P | SV6 | AMP MT CONNECTOR |  |  |  |  |  |  |  |  |  |  |  |  | unknown | unknown | 0
1 |  | L04P | L04P | SV5 | AMP MT CONNECTOR |  |  |  |  |  |  |  |  |  |  |  |  | unknown | unknown | 0
1 |  | MTA02-156 | 1X2MTA | J1 | AMP connector |  |  |  |  |  |  |  |  |  |  |  |  |  |  | 4
1 | 0.1 uF | CPOL-EUSMCB | SMC_B | CAP2 | POLARIZED CAPACITOR, European symbol |  |  |  |  |  |  |  |  |  |  |  |  |  |  | 25 | C
4 | 0.1uf | CPOL-EUSMCB | SMC_B | C2, C6, C10, C14 | POLARIZED CAPACITOR, European symbol |  |  |  |  |  |  |  |  |  |  |  |  |  |  | 25 | C
4 | 0.1uf/250v | C-EU102-054X133 | C102-054X133 | C13, C19, C20, C21 | CAPACITOR, European symbol |  |  |  |  |  |  |  |  |  |  |  |  |  |  | 0 | C
4 | 10k | R-EU_R1206 | R1206 | R32, R34, R36, R38 | RESISTOR, European symbol |  |  |  |  |  |  |  |  |  |  |  |  |  |  | 41 | R
4 | 10pF | C-EUC1206 | C1206 | C4, C8, C12, C16 | CAPACITOR, European symbol |  |  |  |  |  |  |  |  |  |  |  |  |  |  | 54 | C
4 | 10pf | C-EUC1206 | C1206 | C3, C7, C11, C15 | CAPACITOR, European symbol |  |  |  |  |  |  |  |  |  |  |  |  |  |  | 54 | C
1 | 10uF | CPOL-EUSMCB | SMC_B | C18 | POLARIZED CAPACITOR, European symbol |  |  |  |  |  |  |  |  |  |  |  |  |  |  | 25 | C
1 | 2N3904 | 2N3904 | TO92 | T1 | NPN TRANSISTOR |  |  |  |  |  |  |  |  |  |  |  |  |  |  | 27
4 | 300k | R-EU_R1206 | R1206 | R31, R33, R35, R37 | RESISTOR, European symbol |  |  |  |  |  |  |  |  |  |  |  |  |  |  | 41 | R
2 | 330 | R-EU_R0805 | R0805 | R1, R40 | RESISTOR, European symbol |  |  |  |  |  |  |  |  |  |  |  |  |  |  | 86 | R
4 | 5.6k | R-EU_R1206 | R1206 | OUT_A_X, OUT_A_Y, OUT_B_X, OUT_B_Y | RESISTOR, European symbol |  |  |  |  |  |  |  |  |  |  |  |  |  |  | 41 | R
1 | DAC8534IPW | DAC8534IPW | SOP65P640X120-16N | DAC | 2.7V to 5.5V, Quad Channel, 16-Bit, Serial Input DAC | DAC8534IPW | https://www.arrow.com/en/products/dac8534ipw/texas-instruments | 2.7V to 5.5V, Quad Channel, 16-Bit, Serial Input DAC | 1.2mm | Texas Instruments | DAC8534IPW |  | 595-DAC8534IPW | https://www.mouser.com/Search/Refine.aspx?Keyword=595-DAC8534IPW
2 | Green | LEDSMT1206 | 1206 | LED1, POWER | LED |  |  |  |  |  |  |  |  |  |  |  |  |  |  | 20
2 | L293DD | L293DD | SOIC127P1032X265-20N | MOTOR_DRIVER_3, MOTOR_DRIVER_4 | L293DD, Motor Driver, 4.5 36 V, 20-Pin SOIC | L293DD | https://www.arrow.com/en/products/l293dd/stmicroelectronics?region=europe | L293DD, Motor Driver, 4.5 36 V, 20-Pin SOIC | 2.65mm | STMicroelectronics | L293DD |  | 511-L293DD | https://www.mouser.co.uk/ProductDetail/STMicroelectronics/L293DD?qs=m4gxtLzGBzoksItTiSkcgg%3D%3D
2 | MCESL50V107M8X10.5 | MCESL50V107M8X10.5 | CAPAE830X1100N | C1_100UF2, C1_100UF3 | MULTICOMP - MCESL50V107M8X10.5 - CAP, 100F, 50V, RADIAL, SMD |  |  | MULTICOMP - MCESL50V107M8X10.5 - CAP, 100F, 50V, RADIAL, SMD | 11mm | MULTICOMP | MCESL50V107M8X10.5
4 | PA340CC | PA340CC | PA340CC | OP_A_X, OP_A_Y, OP_B_X, OP_B_Y | PA340CC

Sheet: Info
Export Info | Source File
Partlist exported from C:/Users/marti/AppData/Local/Temp/Neutron/ElectronFileOutput/33284/sch-f7afeb61-f5b9-42c0-aa90-607177586d24/PiezoAndMotorBoardV1.1 v1.sch at 05/09/2025 10:40 | PiezoAndMotorBoardV1_1.html

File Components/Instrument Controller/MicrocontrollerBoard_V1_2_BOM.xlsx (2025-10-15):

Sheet: BOM
0 | 1 | 2 | 3 | 4 | 5 | 6 | 7 | 8 | 9
Qty | Value | Device | Footprint Name | Parts | Detailed Description | MF | MPN | OC_FARNELL | OC_NEWARK
2 |  | 34H | 34H | PIEZO_MOTOR_BOARD, PSD_CONVERTER_BOARD | CONNECTOR |  |  | unknown | unknown
1 | PORTENTA_CONNECTOR | PORTENTA_CONNECTOR | DF40C80DS04V51 | U$1

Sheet: Info
Export Info | Source File
Partlist exported from C:/Users/marti/AppData/Local/Temp/Neutron/ElectronFileOutput/33284/sch-642ecabc-9f72-4131-9131-59bdc972c38c/PortentaComputeBoardV1.2 v1.sch at 05/09/2025 10:43 | PortentaComputeBoardV1_2.html

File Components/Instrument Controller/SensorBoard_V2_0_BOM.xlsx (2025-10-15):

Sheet: BOM
0 | 1 | 2 | 3 | 4 | 5 | 6 | 7 | 8 | 9 | 10 | 11 | 12 | 13 | 14 | 15 | 16 | 17 | 18 | 19 | 20 | 21 | 22 | 23 | 24 | 25 | 26 | 27 | 28
Qty | Value | Device | Footprint Name | Parts | Detailed Description | ARROW_PART_NUMBER | ARROW_PRICE-STOCK | CATEGORY | DESCRIPTION | HEIGHT | MANUFACTURER | MANUFACTURER_NAME | MANUFACTURER_PART_NUMBER | MF | MOUSER_PART_NUMBER | MOUSER_PRICE-STOCK | MPN | OC_FARNELL | OC_NEWARK | OPERATING_TEMPERATURE | PART_STATUS | PITCH | POPULARITY | ROHS_COMPLIANCE | SERIES | SPICEPREFIX | SUB-CATEGORY | TYPE
1 |  | 34H | 34H | PL1 | CONNECTOR |  |  |  |  |  |  |  |  |  |  |  |  | unknown | unknown
1 |  | L03P | L03P | SV2 | AMP MT CONNECTOR |  |  |  |  |  |  |  |  |  |  |  |  | unknown | unknown |  |  |  | 0
1 |  | L04P | L04P | SV1 | AMP MT CONNECTOR |  |  |  |  |  |  |  |  |  |  |  |  | unknown | unknown |  |  |  | 0
1 | 0.1 uF | CPOL-EUSMCB | SMC_B | C48 | POLARIZED CAPACITOR, European symbol |  |  |  |  |  |  |  |  |  |  |  |  |  |  |  |  |  | 25 |  |  | C
24 | 0.1uF | C-EUC1206K | C1206K | C3, C4, C5, C6, C9, C10, C14, C15, C18, C19, C26, C27, C30, C31, C32, C33, C34, C41, C43, C51, C52, C54, C57, C58 | CAPACITOR, European symbol |  |  |  |  |  |  |  |  |  |  |  |  |  |  |  |  |  | 13 |  |  | C
5 | 0.1uf | C-EUC1206K | C1206K | C16, C23, C24, C38, C44 | CAPACITOR, European symbol |  |  |  |  |  |  |  |  |  |  |  |  |  |  |  |  |  | 13 |  |  | C
1 | 0.1uf x8r | C-EUC1206K | C1206K | C36 | CAPACITOR, European symbol |  |  |  |  |  |  |  |  |  |  |  |  |  |  |  |  |  | 13 |  |  | C
16 | 1 nF | C-EUC1206K | C1206K | C1, C2, C7, C8, C12, C13, C20, C21, C29, C39, C40, C49, C50, C53, C55, C56 | CAPACITOR, European symbol |  |  |  |  |  |  |  |  |  |  |  |  |  |  |  |  |  | 13 |  |  | C
2 | 1 nf | C-EUC1206K | C1206K | C11, C59 | CAPACITOR, European symbol |  |  |  |  |  |  |  |  |  |  |  |  |  |  |  |  |  | 13 |  |  | C
2 | 10k | R-EU_R0805 | R0805 | R26, R50 | RESISTOR, European symbol |  |  |  |  |  |  |  |  |  |  |  |  |  |  |  |  |  | 86 |  |  | R
6 | 10uf | C-EUC1206K | C1206K | C17, C28, C35, C37, C42, C46 | CAPACITOR, European symbol |  |  |  |  |  |  |  |  |  |  |  |  |  |  |  |  |  | 13 |  |  | C
2 | 10uf 5xr | C-EUC1206K | C1206K | C22, C25 | CAPACITOR, European symbol |  |  |  |  |  |  |  |  |  |  |  |  |  |  |  |  |  | 13 |  |  | C
94 | 15k | R-EU_R0805 | R0805 | R2, R3, R4, R5, R6, R7, R8, R9, R10, R11, R12, R13, R14, R15, R16, R17, R18, R19, R20, R21, R22, R23, R24, R25, R27, R28, R29, R30, R31, R32, R33, R34, R35, R36, R37, R38, R39, R40, R41, R42, R43, R44, R45, R46, R47, R48, R49, R51, R52, R53, R54, R55, R56, R57, R58, R59, R60, R61, R62, R63, R64, R65, R66, R67, R68, R69, R70, R71, R72, R73, R75, R77, R78, R79, R80, R81, R82, R83, R84, R85, R86, R87, R88, R89, R90, R91, R92, R93, R94, R95, R96, R97, R98, R99 | RESISTOR, European symbol |  |  |  |  |  |  |  |  |  |  |  |  |  |  |  |  |  | 86 |  |  | R
2 | 2.7 k | R-EU_R0805 | R0805 | R1, R74 | RESISTOR, European symbol |  |  |  |  |  |  |  |  |  |  |  |  |  |  |  |  |  | 86 |  |  | R
1 | 330 | R-EU_R0805 | R0805 | R76 | RESISTOR, European symbol |  |  |  |  |  |  |  |  |  |  |  |  |  |  |  |  |  | 86 |  |  | R
4 | 5749231-1 | 5749231-1 | 57492311 | FORCE_B_CONN, J7, J8, J9 | DIN Connectors, Mini DIN, Receptacle, Wire-to-Board, 6 Position, Fully Loaded, Mating Alignment, Keyed Mating Alignment Type, PCB Mount Retention | 5749231-1 | https://www.arrow.com/en/products/5749231-1/te-connectivity |  | DIN Connectors, Mini DIN, Receptacle, Wire-to-Board, 6 Position, Fully Loaded, Mating Alignment, Keyed Mating Alignment Type, PCB Mount Retention | 13mm |  | TE Connectivity | 5749231-1 |  | 571-5749231-1 | https://www.mouser.co.uk/ProductDetail/TE-Connectivity/5749231-1?qs=BU%252BKxOECzi5wkFfxZKXzRw%3D%3D
1 | AD7616BSTZ-RL | AD7616BSTZ-RL | QFP65P1600X1600X160-80N | IC5 | Data Acquisition ADCs/DACs - Specialized 100ksps 16 ch muxed Dual 16B SAR ADC | AD7616BSTZ-RL | https://www.arrow.com/en/products/ad7616bstz-rl/analog-devices?region=nac |  | Data Acquisition ADCs/DACs - Specialized 100ksps 16 ch muxed Dual 16B SAR ADC | 1.6mm |  | Analog Devices | AD7616BSTZ-RL |  | 584-AD7616BSTZ-RL | https://www.mouser.co.uk/ProductDetail/Analog-Devices/AD7616BSTZ-RL?qs=k%252BwXAfPrzCkcGjw73paKug%3D%3D
1 | Green | LEDSMT1206 | 1206 | LED1 | LED |  |  |  |  |  |  |  |  |  |  |  |  |  |  |  |  |  | 20
2 | MCESL50V107M8X10.5 | MCESL50V107M8X10.5 | CAPAE830X1100N | C45, C47 | MULTICOMP - MCESL50V107M8X10.5 - CAP, 100F, 50V, RADIAL, SMD |  |  |  | MULTICOMP - MCESL50V107M8X10.5 - CAP, 100F, 50V, RADIAL, SMD | 11mm |  | MULTICOMP | MCESL50V107M8X10.5
8 | OPA4228UA | OPA4228UA | SOIC127P600X175-14N | IC1, IC2, IC3, IC4, IC6, IC7, IC8, IC9 | OPA4228UA, Quad Operational Amplifier 8MHz, 14-Pin SOIC | OPA4228UA | https://www.arrow.com/en/products/opa4228ua/texas-instruments?region=nac |  | OPA4228UA, Quad Operational Amplifier 8MHz, 14-Pin SOIC | 1.75mm |  | Texas Instruments | OPA4228UA |  | 595-OPA4228UA | https://www.mouser.co.uk/ProductDetail/Texas-Instruments/OPA4228UA?qs=7nS3%252BbEUL6uF7N9V22cRlw%3D%3D
2 | PINHD-1X55X2MM | PINHD-1X55X2MM | 1_05X2MM | EXTERNAL_FORCE_A, EXTERNAL_FORCE_B | PIN HEADER |  |  | Headers | Header, Straight, 5 Position |  | Generic |  |  |  |  |  | Generic |  |  | Generic | Active | 0.079" (2.00mm) |  | Generic | Generic |  | Headers, Male Pins | Board to Board or Cable, Unshrouded, Through Hole, Straight

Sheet: Info
Export Info | Source File
Partlist exported from C:/Users/marti/AppData/Local/Temp/Neutron/ElectronFileOutput/33284/sch-947f09bf-726e-4e46-9619-54ccb33ccec7/PSD2DACV2.0 v16.sch at 05/09/2025 10:45 | PSD2DACV2_0.html

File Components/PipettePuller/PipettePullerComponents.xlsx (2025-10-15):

Name | Part number | Vendor | Required | Cost ($) | Comment
Base | MB1015/M | Thorlabs | 1 | 50
Post | TR150/M (https://www.thorlabs.com/thorproduct.cfm?partnumber=TR150/M) | Thorlabs | 2 | 9
Screw | M4 - ca 40 mm |  | 5 | 1 | Any M4 screws of approximately the correct length will work. Recommend buying a screw set from e.g. Thorlabs HW-KIT1/M
Nuts | M4 nuts |  | 5 | 1
BNC connectors |  |  | 2
BNC cables |  |  | 2
Platina wire | 039383-BS | ThermoFischer | 1 | 100 | 10 cm is sufficient
Programmable Benchtop DC Power supply | TENMA 72-2540 | Newark/Farnell | 1 | 200 | The provided software is compatible with TENMA power supplies, may need adapting for comaptability with other PSU units. PSU needs to be able to provide at least 4A.
Clamp | PullerClampBlock.stl | 3D print | 2 | 1 | 3D print stl file
Puller bottom | PullerBottom.stl | 3D print | 1 | 1 | 3D print stl file
Puller middle | PullerMiddle.stl | 3D print | 1 | 1 | 3D print stl file
Puller top | PullerTop.stl | 3D print | 1 | 1 | 3D print stl file

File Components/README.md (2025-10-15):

# Excel files with lists of the components needed for the different parts of the system

## ComponentList contains the following
 - List of the components needed for the optical tweezers instrument, based on the minitweezers design <http://tweezerslab.unipr.it/cgi-bin/home.pl>
 - List of components needed for the controller power supply.
 - List of the equipment needed to run the instrument, such as the host computer.

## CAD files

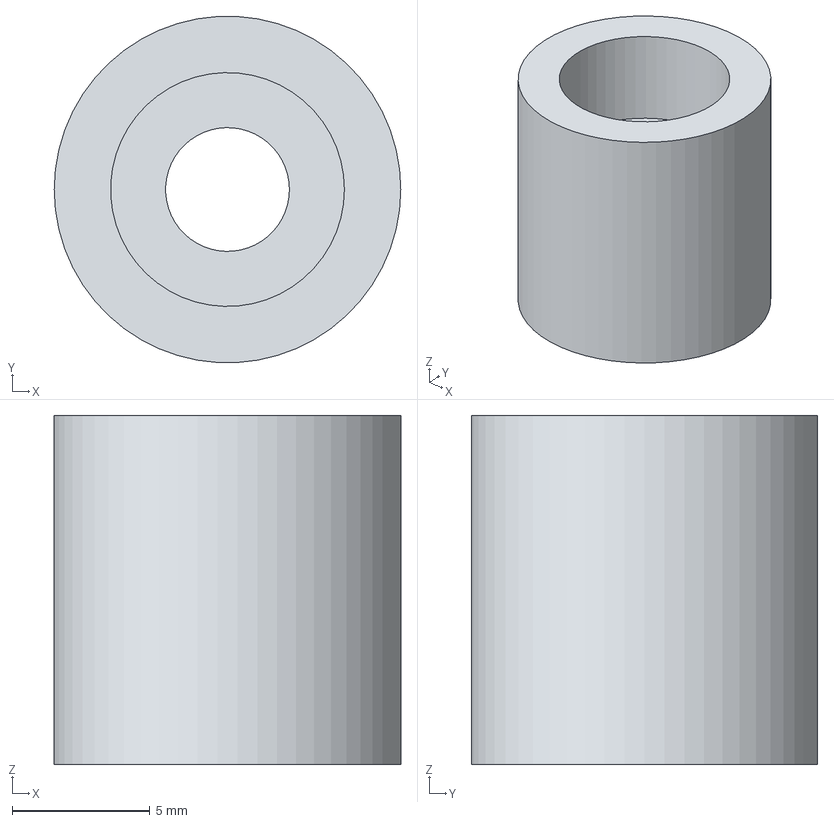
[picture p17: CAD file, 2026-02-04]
Components/Custom mechanical components/PSD holder handle updated.step
12.6 x 12.6 x 12.7 mm

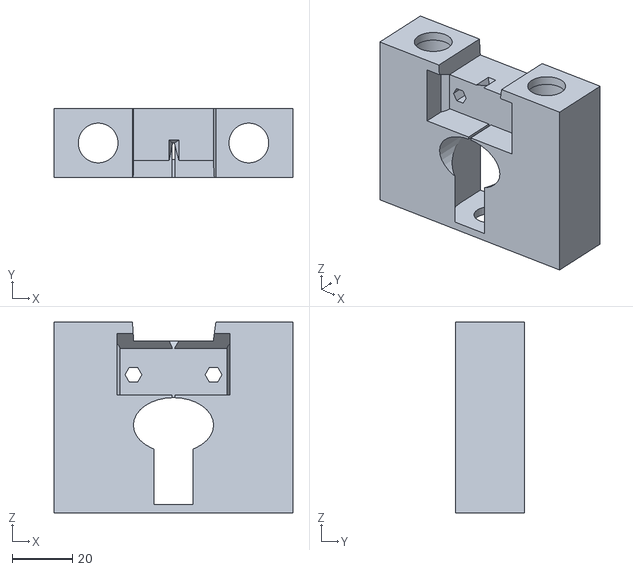
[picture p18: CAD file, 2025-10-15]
Components/PipettePuller/PullerBottom.stl
79.3 x 22.9 x 63.3

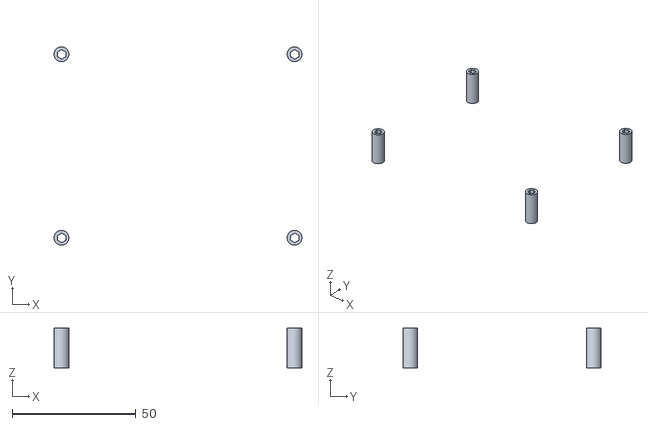
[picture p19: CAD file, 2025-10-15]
Instrument Schematics/PCB_spacers.stl
100.0 x 80.0 x 16.1

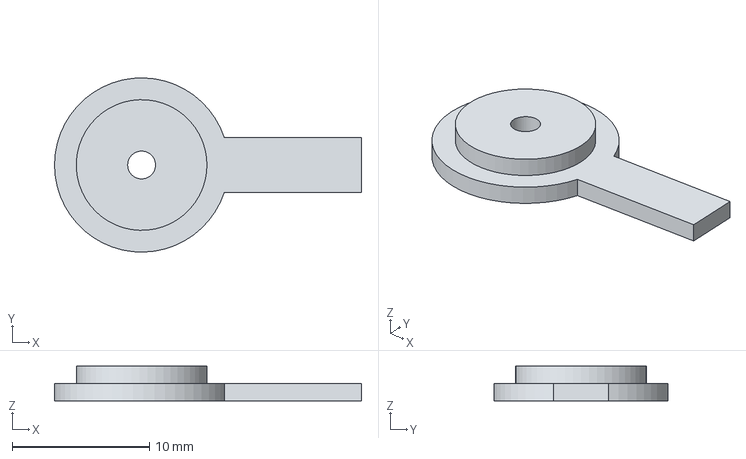
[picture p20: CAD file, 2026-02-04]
Components/Custom mechanical components/Aperture Iris Button updated.step
22.4 x 12.7 x 2.54 mm

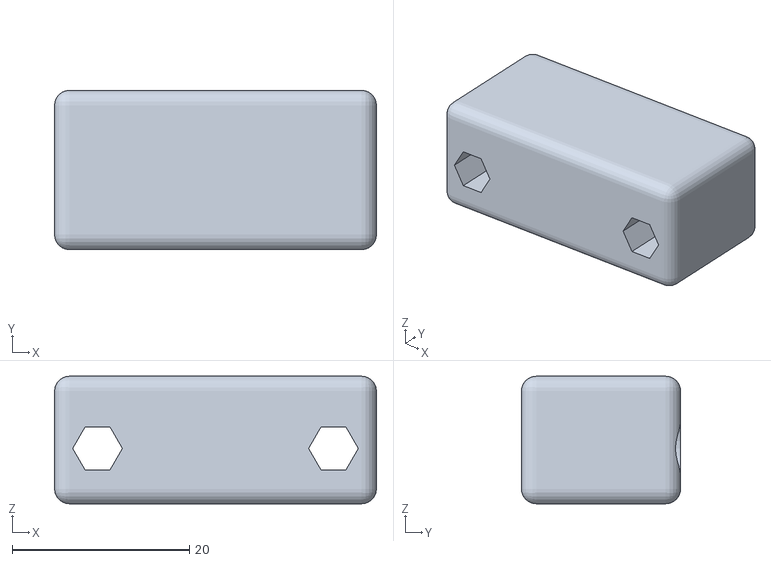
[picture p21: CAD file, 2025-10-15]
Components/PipettePuller/PullerClampBlock.stl
36.3 x 18.0 x 14.4

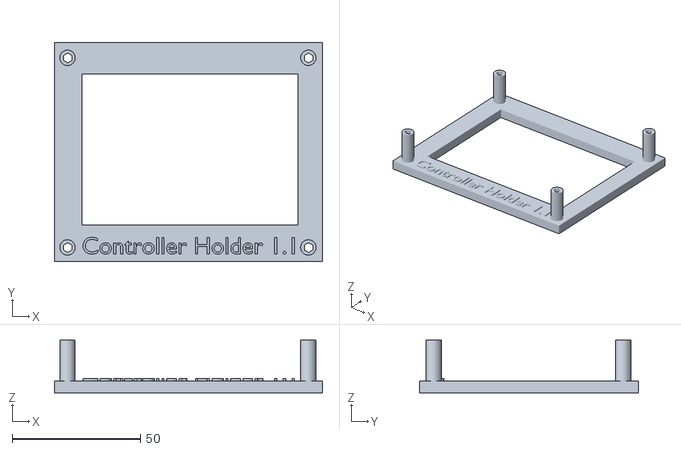
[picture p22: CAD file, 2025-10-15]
Instrument Schematics/ControllerStand.stl
104.6 x 85.4 x 20.5

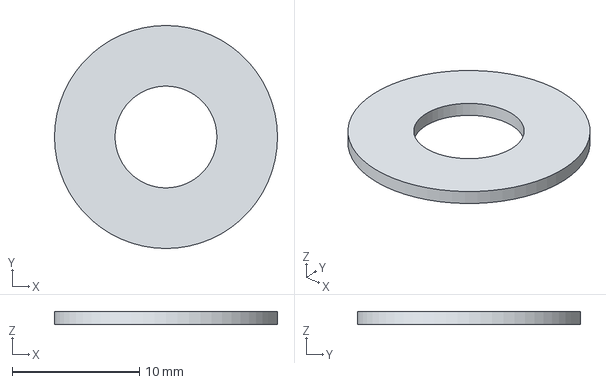
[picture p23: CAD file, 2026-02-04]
Components/Custom mechanical components/Filter holder disc-updated.step
17.5 x 17.5 x 1.00 mm

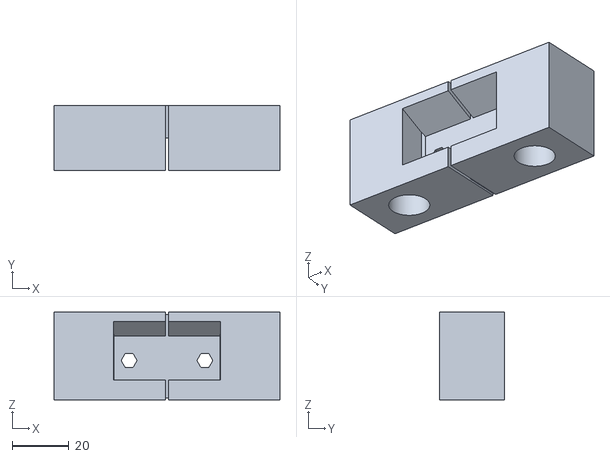
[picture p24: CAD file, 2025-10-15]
Components/PipettePuller/PullerTop.stl
79.3 x 22.9 x 30.8

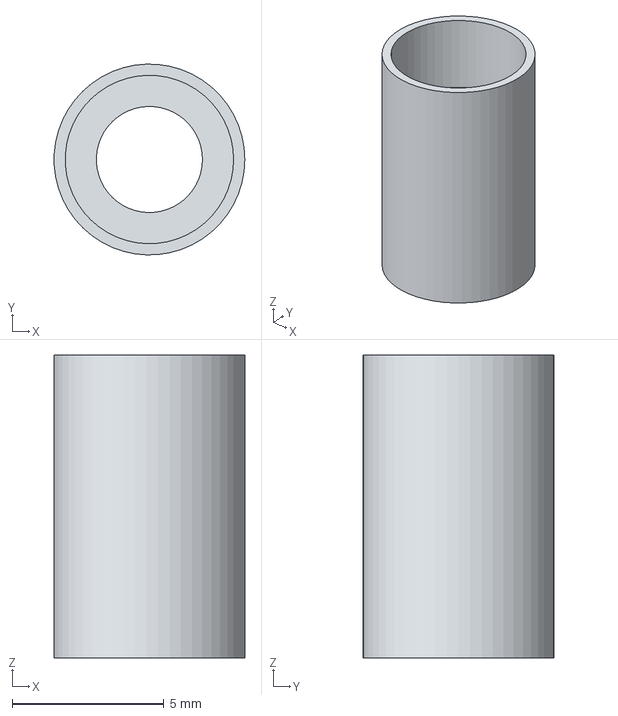
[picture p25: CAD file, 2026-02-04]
Components/Custom mechanical components/Chamber holder pin updated.step
6.29 x 6.30 x 10.0 mm

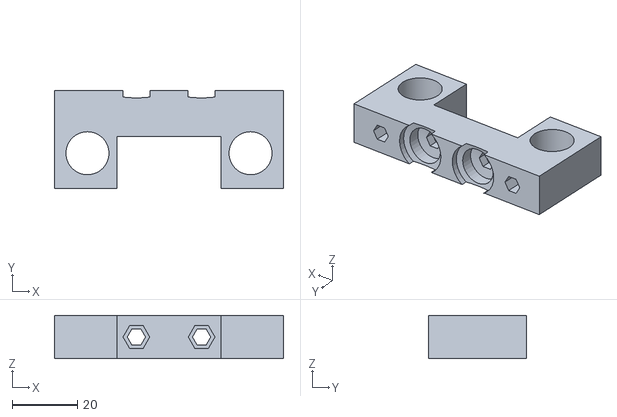
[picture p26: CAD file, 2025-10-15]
Components/PipettePuller/PullerMiddle.stl
70.2 x 29.9 x 13.3

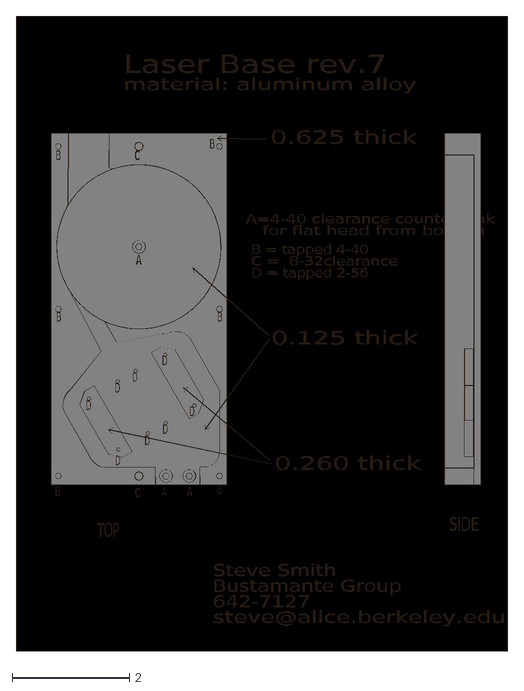
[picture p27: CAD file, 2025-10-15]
Components/Custom mechanical components/laser base mill cut7.dxf
A
B
C
D
A=4-40 clearance countersunk
for flat head from bottom
B = tapped 4-40
C = 8-32clearance
D = tapped 2-56
Laser Base rev.7
material: aluminum alloy
Steve Smith
Bustamante Group
642-7127
steve@alice.berkeley.edu
0.125 thick
0.625 thick
0.260 thick
TOP
SIDE

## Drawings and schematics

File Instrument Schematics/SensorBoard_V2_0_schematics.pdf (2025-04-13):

GND | -15V +15V
GND MCESL50V¹⁰⁷M⁸X¹⁰.5 | MCESL50V¹⁰⁷M⁸X¹⁰.5

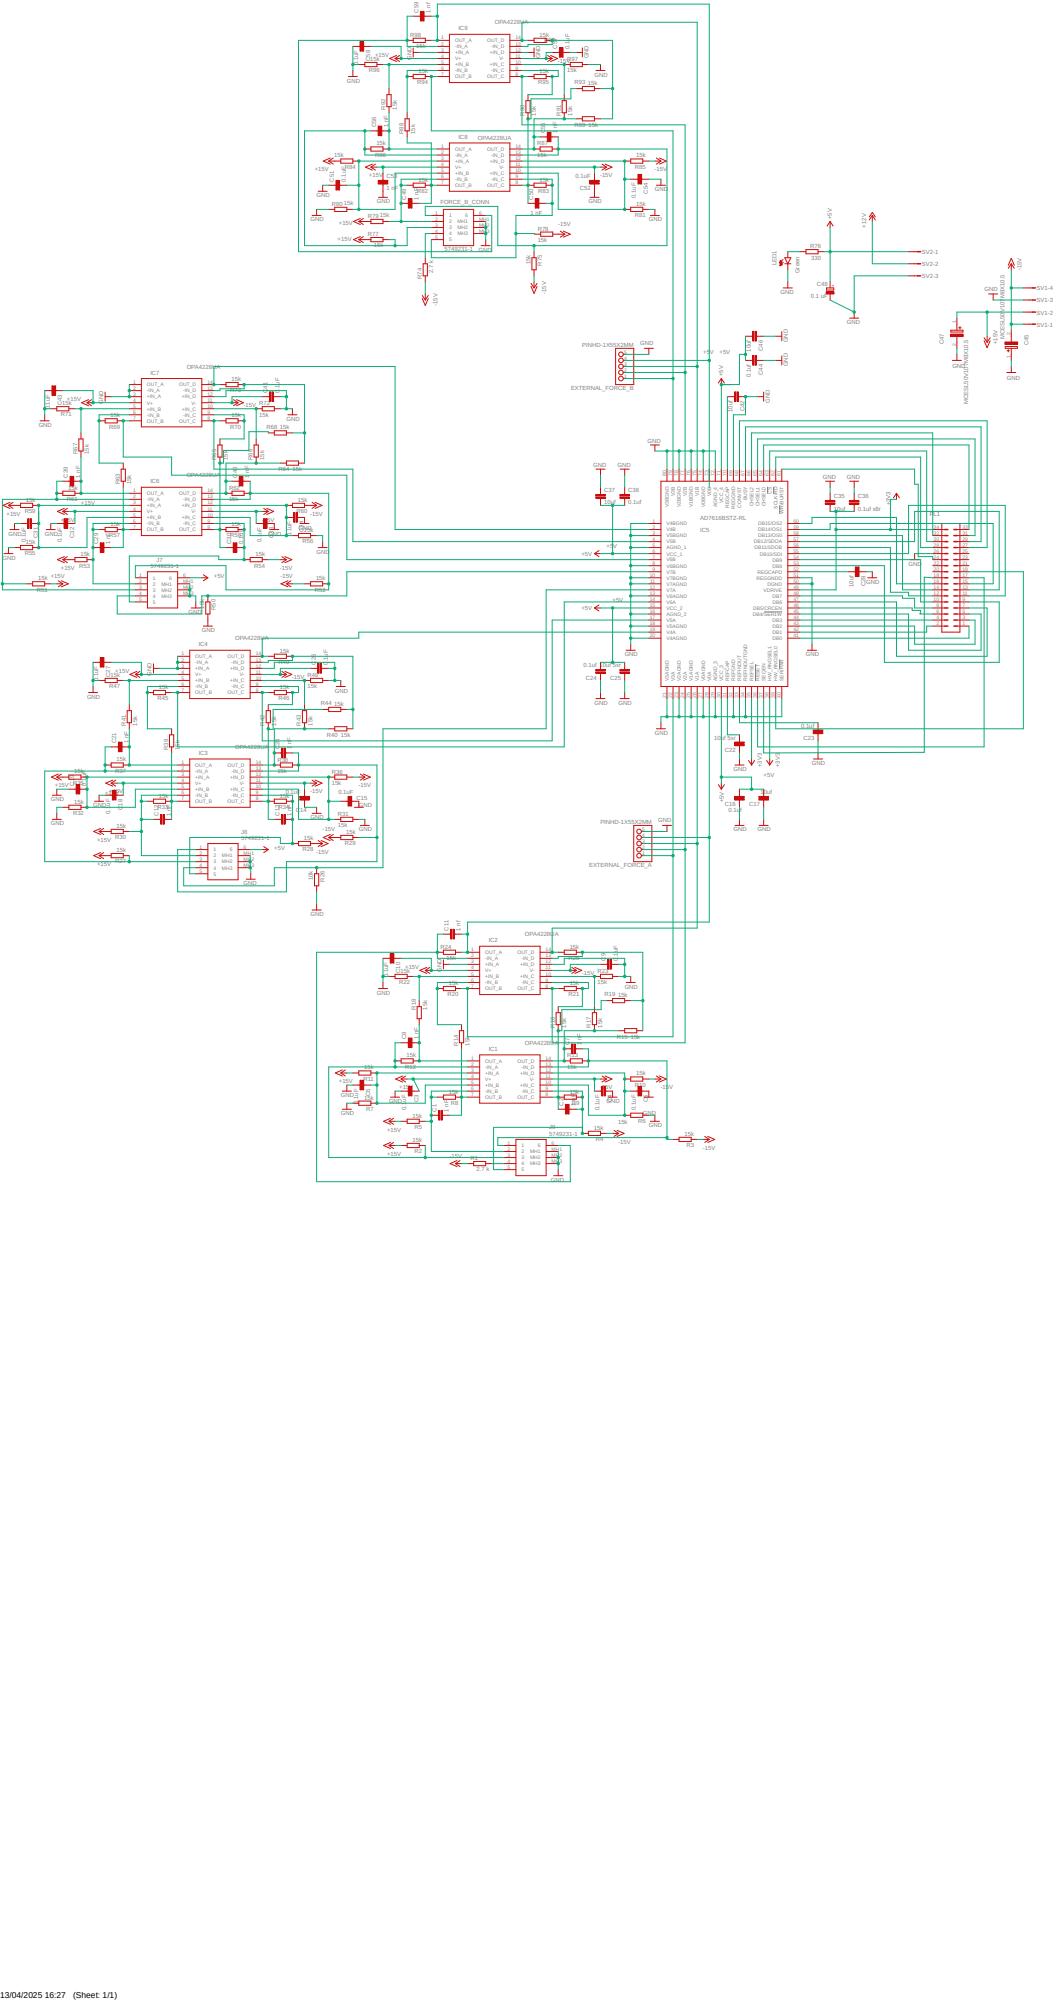
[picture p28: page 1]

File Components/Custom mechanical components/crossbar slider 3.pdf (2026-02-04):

# Cross-bar Slider rev 3

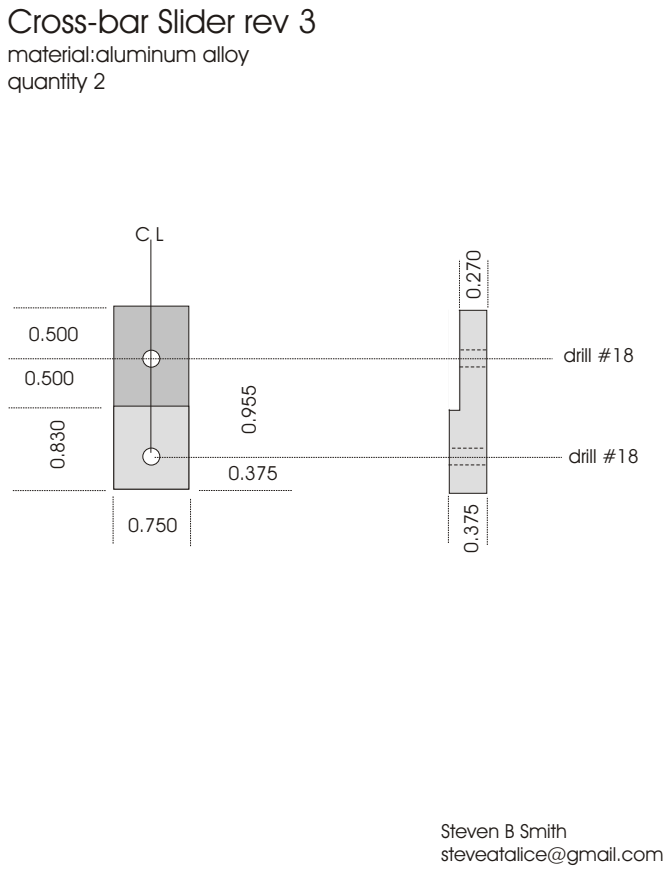
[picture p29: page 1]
drill #18

material:aluminum alloy
quantity 2

Steven B Smith
steveatalice@gmail.com

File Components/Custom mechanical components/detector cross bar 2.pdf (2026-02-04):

# Detector Cross Bar rev. 2

# material: Aluminum alloy

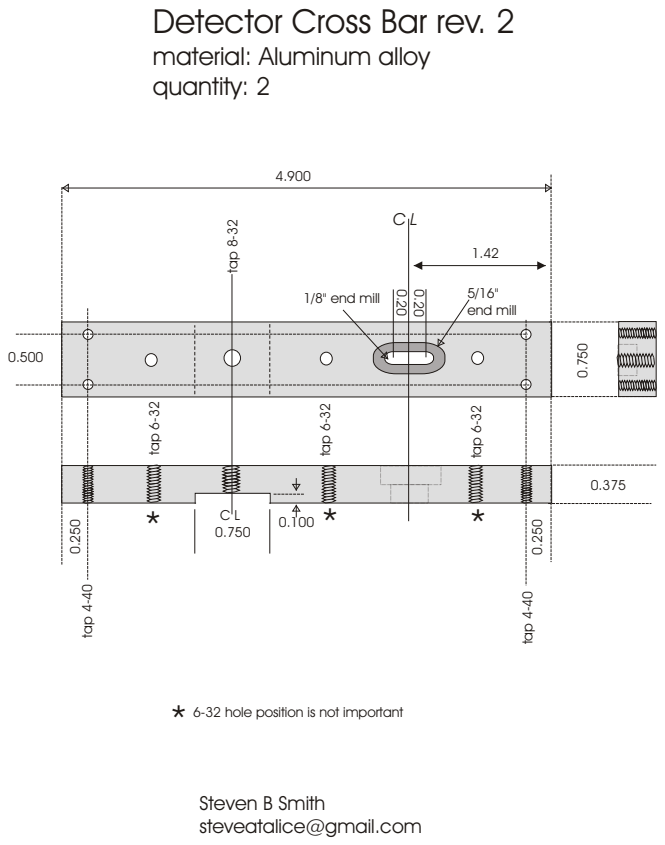
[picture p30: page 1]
quantity: 2; 5/16" end mill; 1/8" end mill

6-32 hole position is not important

Steven B Smith
steveatalice@gmail.com

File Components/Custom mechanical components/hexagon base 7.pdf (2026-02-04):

# Hexagon Base

## material: 1/4" thick

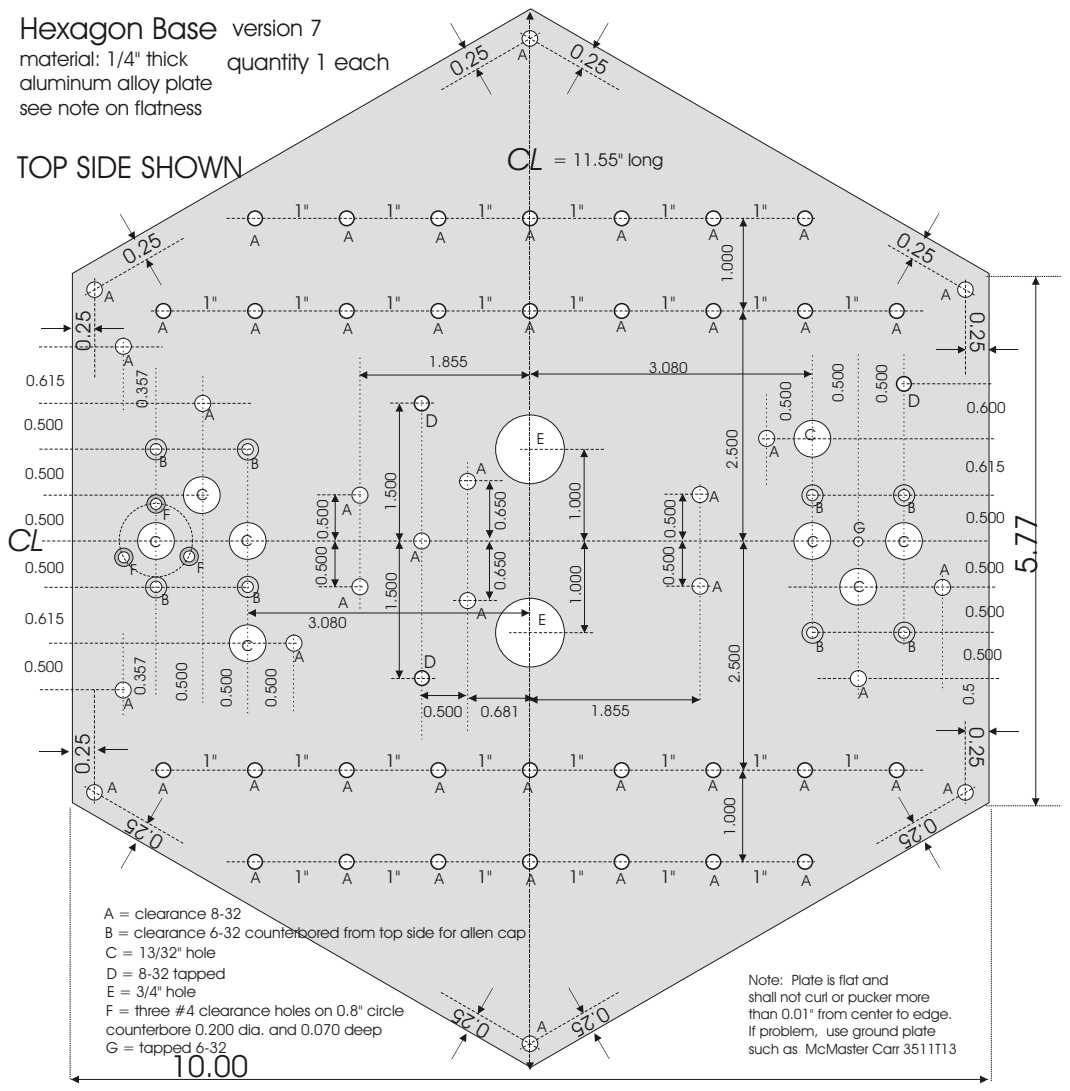
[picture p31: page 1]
CL = 11.55" long; version 7 quantity 1 each

aluminum alloy plate
see note on flatness
TOP SIDE SHOWN

A = clearance 8-32
B = clearance 6-32 counterbored from top side for allen cap
C = 13/32" hole
D = 8-32 tapped
E = 3/4" hole
F = three #4 clearance holes on 0.8" circle
counterbore 0.200 dia. and 0.070 deep
G = tapped 6-32

Note: Plate is flat and
shall not curl or pucker more
than 0.01" from center to edge.
If problem, use ground plate
such as McMaster Carr 3511T13

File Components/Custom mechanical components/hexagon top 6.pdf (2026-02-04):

# Hexagon Top ver. 6 material: 1/4" thick

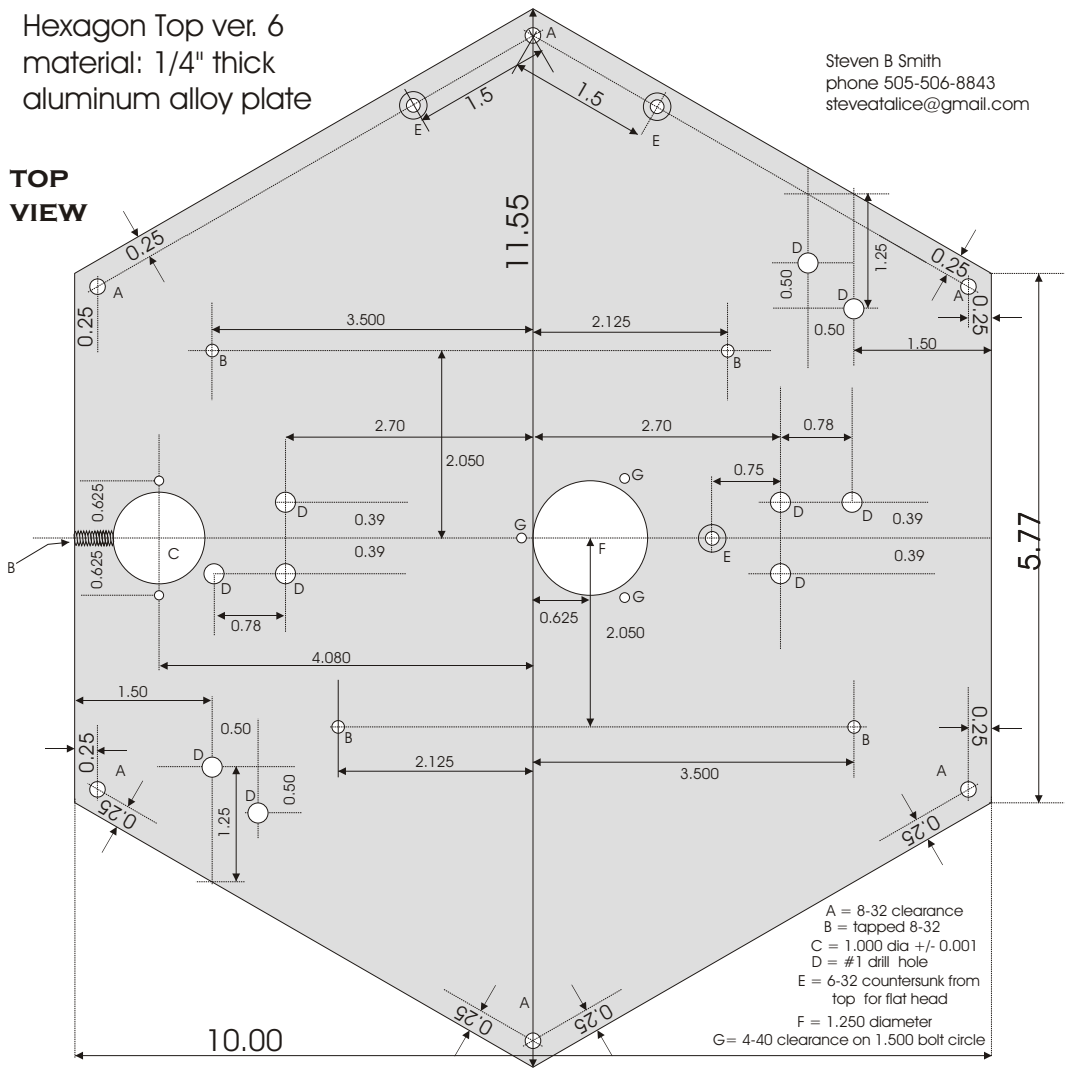
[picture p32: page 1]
top; view

Steven B Smith
phone 505-506-8843
steveatalice@gmail.com

aluminum alloy plate

A = 8-32 clearance
B = tapped 8-32
C = 1.000 dia +/- 0.001
D = #1 drill hole
E = 6-32 countersunk from
top for flat head
F = 1.250 diameter

G= 4-40 clearance on 1.500 bolt circle

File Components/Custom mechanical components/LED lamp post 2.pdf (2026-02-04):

# LED lamp post foot

## material: aluminum alloy

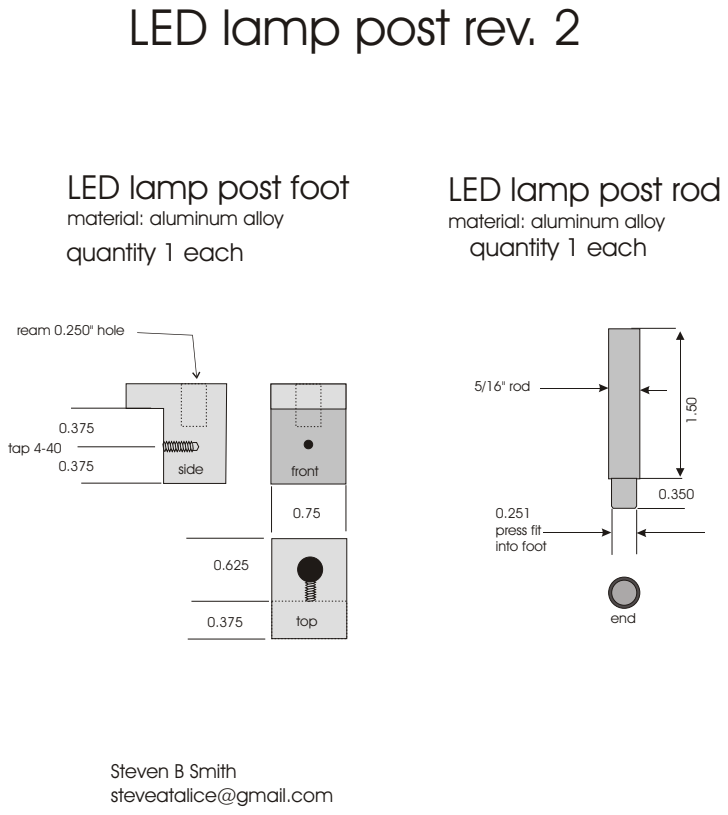
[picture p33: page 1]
5/16" rod; 0.251 press fit into foot; quantity 1 each; ream 0.250" hole; side; front; top; tap 4-40; end

LED lamp post rev. 2

LED lamp post rod

material: aluminum alloy

Steven B Smith
steveatalice@gmail.com

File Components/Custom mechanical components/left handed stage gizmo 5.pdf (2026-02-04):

# Left-handed Stage Gizmo Ver.5 material: stainless steel

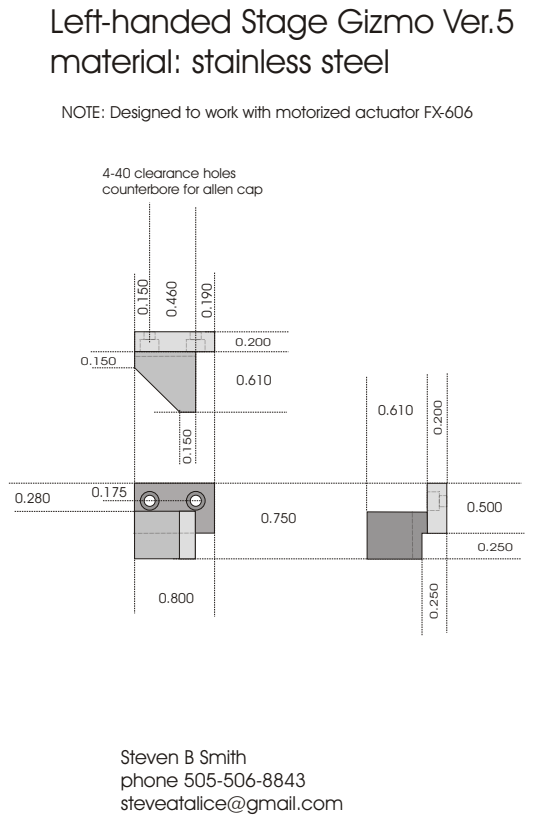
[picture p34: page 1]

NOTE: Designed to work with motorized actuator FX-606

4-40 clearance holes
counterbore for allen cap

Steven B Smith
phone 505-506-8843
steveatalice@gmail.com

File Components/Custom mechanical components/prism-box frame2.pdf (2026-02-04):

# Prism-box Frame ver.2 material: aluminum 6061

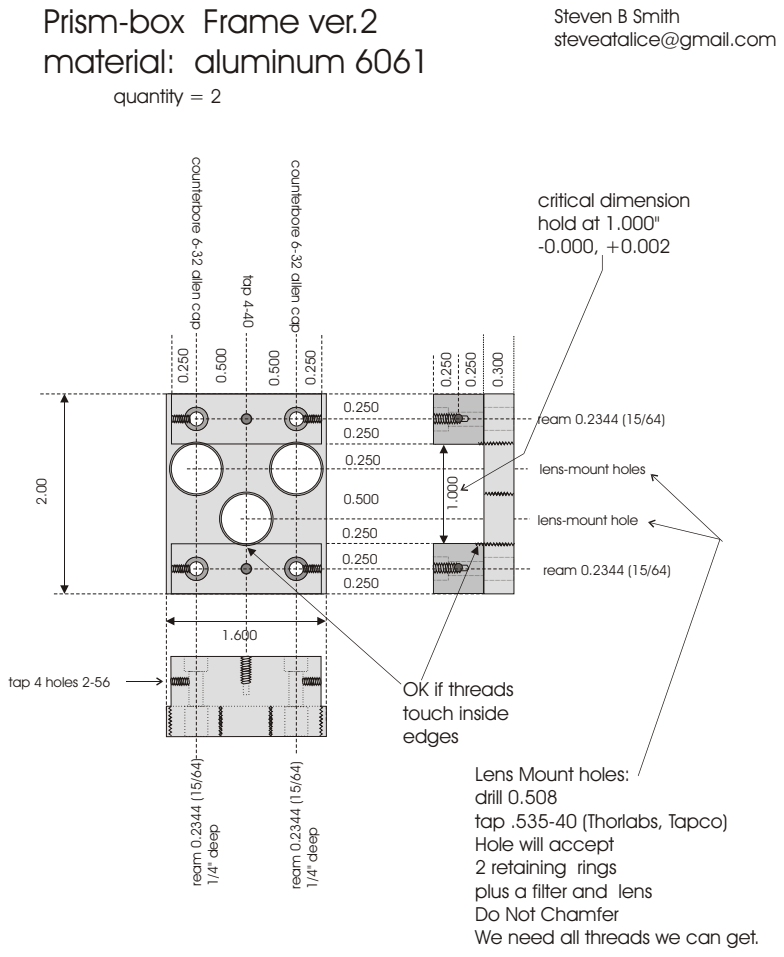
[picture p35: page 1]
ream 0.2344 (15/64); tap 4 holes 2-56; critical dimension hold at 1.000" -0.000, +0.002; c o unterb; ore; 6-32 allen c; quantity = 2

Steven B Smith
steveatalice@gmail.com

lens-mount holes

lens-mount hole

OK if threads
touch inside
edges

Lens Mount holes:
drill 0.508
tap .535-40 (Thorlabs, Tapco)
Hole will accept
2 retaining rings
plus a filter and lens
Do Not Chamfer
We need all threads we can get.

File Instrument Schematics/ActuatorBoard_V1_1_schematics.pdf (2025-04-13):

# 5.6k ⁻¹⁵V

# GND GNDGND GNDGND

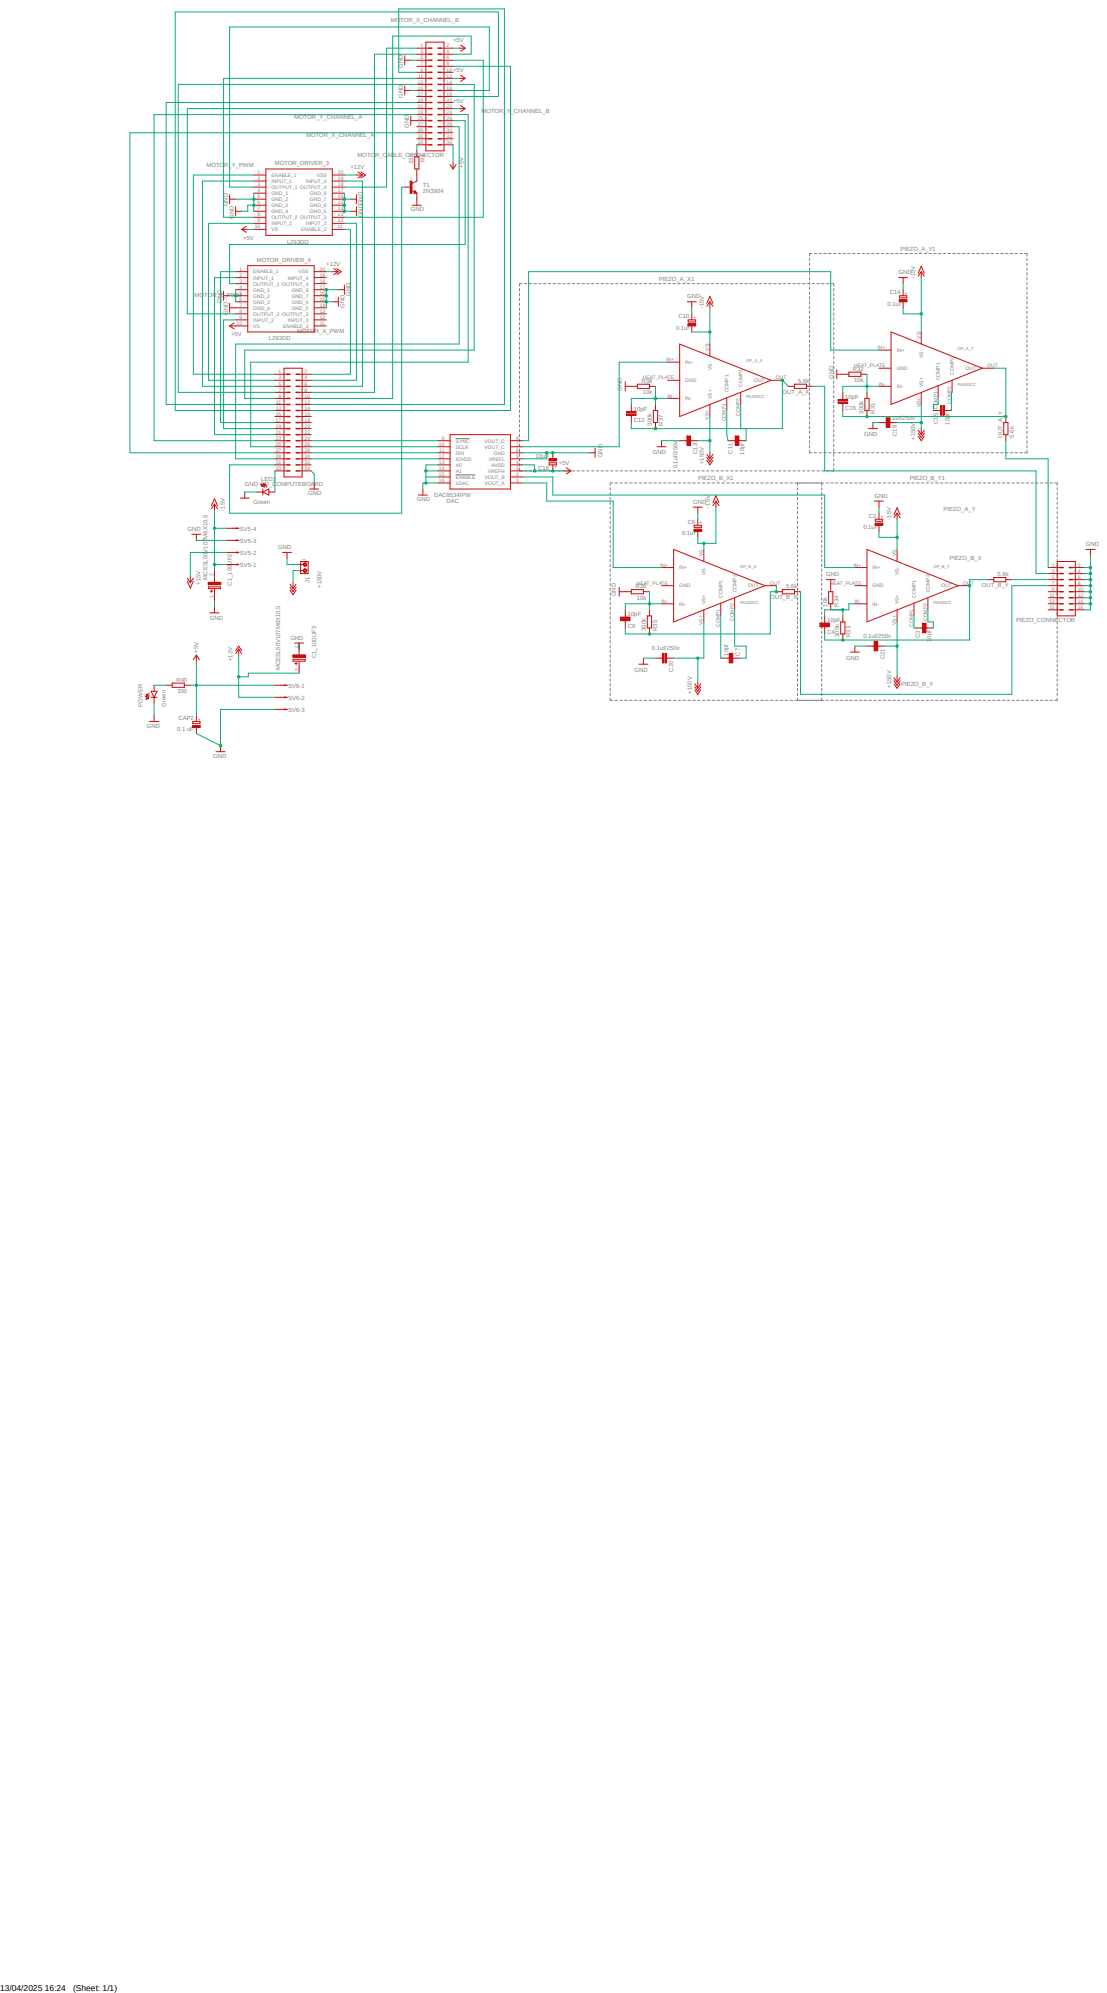
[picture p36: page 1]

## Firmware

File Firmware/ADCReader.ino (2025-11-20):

/*
Arduino sketch for reading the AD7616 analog digital converted using an arduino portenta.
Uses the parallel interface of the ADC.
*/
#define SEQEN       PI_10
#define RESET       PI_13
#define WR_BURST    PH_10
#define SCLK_RD     PH_12
#define CS          PI_4


#define CHSEL0      PI_7
#define CHSEL1      PI_5
#define CHSEL2      PC_13

#define HW_RNGSEL0  PA_4

#define AD_BUSY     PI_6
#define CONVST      PH_6

#define DB0         PB_15
#define DB1         PH_9
#define DB2         PB_3
#define DB3         PH_11
#define DB4         PB_4
#define DB5         PH_14
#define DB6         PB_14
#define DB7         PJ_8
#define DB8         PD_7
#define DB9         PA_11
#define DB10        PD_6
#define DB11        PG_14
#define DB12        PD_3
#define DB13        PG_9
#define DB14        PB_9
#define DB15        PI_2


#define READ_PIN(port, bit, outbit) (((port >> bit) & 1) << outbit)

void setup_ADC() {
  /*
  Initiates the analog digital convertedr by setting the various pins to their correct values
  and modes.
  */
  pinMode(LED_BUILTIN, OUTPUT);

  // Initalize the pins to output/input
  pinMode(SEQEN, OUTPUT);
  pinMode(RESET, OUTPUT);
  pinMode(WR_BURST, OUTPUT);
  pinMode(SCLK_RD, OUTPUT);
  pinMode(CS, OUTPUT);

  pinMode(HW_RNGSEL0, OUTPUT);

  pinMode(CHSEL0, OUTPUT);
  pinMode(CHSEL1, OUTPUT);
  pinMode(CHSEL2, OUTPUT);
  pinMode(AD_BUSY, INPUT);
  pinMode(CONVST, OUTPUT);

  // Set the paralell input pins
  pinMode(DB0,INPUT_PULLUP);  // Used to have just input on all these
  pinMode(DB1,INPUT_PULLUP);
  pinMode(DB2,INPUT_PULLUP);
  pinMode(DB3,INPUT_PULLUP);
  pinMode(DB4,INPUT_PULLUP);
  pinMode(DB5,INPUT_PULLUP);
  pinMode(DB6,INPUT_PULLUP);
  pinMode(DB7,INPUT_PULLUP);
  pinMode(DB8,INPUT_PULLUP);
  pinMode(DB9,INPUT_PULLUP);
  pinMode(DB10,INPUT_PULLUP);
  pinMode(DB11,INPUT_PULLUP);
  pinMode(DB12,INPUT_PULLUP);
  pinMode(DB13,INPUT_PULLUP);
  pinMode(DB14,INPUT_PULLUP);
  pinMode(DB15,INPUT_PULLUP);

  // Select channel 0
  digitalWrite(CHSEL0,LOW);
  digitalWrite(CHSEL1,LOW);
  digitalWrite(CHSEL2,LOW);

  // Set read range of the ADC to +- 10V, (HIGH), for +- 5V Set low.
  digitalWrite(HW_RNGSEL0, HIGH);

  //Set RD and CS high(default mode)
  digitalWrite(SCLK_RD,HIGH);
  digitalWrite(CS,HIGH);

  // Internal reference, Tied high on board
  digitalWrite(WR_BURST, LOW);
  digitalWrite(SEQEN, LOW); // Enable sequencer, hardware mode only

  // Activate the ADC pin by setting the reset pin high after having had it low
  digitalWrite(RESET, LOW);
  delay(100);
  digitalWrite(RESET, HIGH);
}

void sampleDataUint8(uint8_t* data_array, uint16_t msb_idx, uint16_t lsb_idx)
{
    /*
    Samples a single channel of the ADC and puts the result in the data array.
    */

    // Prefetch all relevant ports once
    
    uint32_t A = GPIOA->IDR;
    uint32_t B = GPIOB->IDR;
    uint32_t D = GPIOD->IDR;
    uint32_t G = GPIOG->IDR;
    uint32_t H = GPIOH->IDR;
    uint32_t I = GPIOI->IDR;
    uint32_t J = GPIOJ->IDR;
    
    // Clear target bytes
    data_array[lsb_idx] = 0;
    data_array[msb_idx] = 0;

    // --- LSB byte ---
    data_array[lsb_idx] =
          READ_PIN(B,15,0)
        | READ_PIN(H,9,1)
        | READ_PIN(B,3,2)
        | READ_PIN(H,11,3)
        | READ_PIN(B,4,4)
        | READ_PIN(H,14,5)
        | READ_PIN(B,14,6)
        | READ_PIN(J,8,7);

    // --- MSB byte ---
    data_array[msb_idx] =
          READ_PIN(D,7,0)
        | READ_PIN(A,11,1)
        | READ_PIN(D,6,2)
        | READ_PIN(G,14,3)
        | READ_PIN(D,3,4)
        | READ_PIN(G,9,5)
        | READ_PIN(B,9,6);

    // Optional flag bit (bit 7 of MSB)
    if (((I >> 2) & 1) == 0) {
        data_array[msb_idx] |= (1 << 7);
    }
}

void select_channel_fast(uint8_t channel_pair) {
  /*
  Selects the target channel on the ADC for sampling
  */
  switch (channel_pair) {
    case 0:
      GPIOI->BSRR = (1 << (7 + 16));
      GPIOI->BSRR = (1 << (5 + 16));
      GPIOC->BSRR = (1 << (13 + 16));
      break;

    case 1:
      GPIOI->BSRR = (1 << 7);
      GPIOI->BSRR = (1 << (5 + 16));
      GPIOC->BSRR = (1 << (13 + 16));
      break;

    case 2:
      GPIOI->BSRR = (1 << (7 + 16));
      GPIOI->BSRR = (1 << 5);
      GPIOC->BSRR = (1 << (13 + 16));
      break;

    case 3:
      GPIOI->BSRR = (1 << 7);
      GPIOI->BSRR = (1 << 5);
      GPIOC->BSRR = (1 << (13 + 16));
      break;

    case 4:
      GPIOI->BSRR = (1 << (7 + 16));
      GPIOI->BSRR = (1 << (5 + 16));
      GPIOC->BSRR = (1 << 13);
      break;

    case 5:
      GPIOI->BSRR = (1 << 7);
      GPIOI->BSRR = (1 << (5 + 16));
      GPIOC->BSRR = (1 << 13);
      break;

    case 6:
      GPIOI->BSRR = (1 << (7 + 16));
      GPIOI->BSRR = (1 << 5);
      GPIOC->BSRR = (1 << 13);
      break;

    case 7:
      GPIOI->BSRR = (1 << 7);
      GPIOI->BSRR = (1 << 5);
      GPIOC->BSRR = (1 << 13);
      break;

    default:
      return;
  }
}


void read_adc_2_uint8_t(uint8_t channel_pair, uint8_t* data_array, uint16_t index1, uint16_t index2){
  /*
  Reads a pair of channels (A and B) on the analog digital converter and puts the result in the data_array
  */
  if (channel_pair>7){
    return;
  }
  // Select the channel to sample during the next cycle(not this one)
  select_channel_fast((channel_pair+1)%8);
  
  GPIOH->BSRR = (1 << 6);
  GPIOH->BSRR = (1 << (6 + 16));
  uint8_t lim = 0;
  while (((GPIOI->IDR & (1 << 6)) >> 6) && lim<200){
    lim+=1;
  }
  
  GPIOI->BSRR = (1 << (4 + 16));
  GPIOH->BSRR = (1 << (12 + 16));
  
  sampleDataUint8(data_array, index1+1, index1);

  GPIOH->BSRR = (1 << 12);
  GPIOI->BSRR = (1 << 4);

  GPIOI->BSRR = (1 << (4 + 16));
  GPIOH->BSRR = (1 << (12 + 16));

  sampleDataUint8(data_array, index2+1, index2);
  GPIOI->BSRR = (1 << 4);
  GPIOH->BSRR = (1 << 12);
}

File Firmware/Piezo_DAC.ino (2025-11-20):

#define LDAC	         PE_2 // Needs to be put low, used if all outputs are to be changed at the same time
#define IOVDD_DAC      PI_3 // external power 
#define SPI_SYNC       PJ_9 //UART3 RX PIN
#define AUTO_ALIGN_LIM 0  // 40 is standard, seem to work fine. Used 20 before


#define AX  0.0501
#define AY  0.0513
#define BX  0.0551
#define BY  0.0574

#define ABX = 0.91
#define ABY = 0.89
#define BAX = 1.10
#define BAY = 1.12


float CONSTANT_FORCE_FAC = -0.02;
float AUTOALIGN_FAC = 0.0002;

float local_align_fac = 0;
float dist_x = 0;
float dist_y = 0;
int force_difference = 0; // Used in the constant force protocol to estimate the difference between current and target force in piezo steps.
uint16_t DAC_pos = 32768; // Variable used to for the DAC position in uint16 instead of 2 x uint8 
long move_counter = 0;


SPI spi(PC_3, PC_2, PI_1);

void setup_DAC() {
  pinMode(SPI_SYNC, OUTPUT);
  pinMode(LED_BUILTIN, OUTPUT);
  GPIOJ->MODER |= (1 << (9 * 2)); // set sync as output pin

  pinMode(IOVDD_DAC,OUTPUT);
  digitalWrite(IOVDD_DAC, HIGH);
  pinMode(LDAC, OUTPUT);
  digitalWrite(LDAC, LOW);
  spi.frequency(25000000);           // Set up your frequency. Max is 25 MHz according to datasheet when operating at a logic voltage level of 3.4V as the portenta does.
  spi.format(8, 3);                  // Messege length (bits), SPI_MODE - check these in your SPI decice's data sheet.
}

void writeNumberFast(uint8_t DACData[]){
  /*
  Writes a number to the DAC. 
  Does this rather fast, at 25 MHz we can write all the 4 channels in ca 10 microseconds.
   */
  GPIOJ->ODR &= ~(1 << 9); // set sync low
  spi.write((const char*)DACData, 3, NULL, 0);
  GPIOJ->ODR |= (1 << 9); // set sync high
}

void autoalign(uint8_t trap){
  /*
  Moves one trap to match the position of the other by reducing the difference in the force reading between the two
  */
  // Trap = 0 => move trap A to match trap B
  local_align_fac = AUTOALIGN_FAC*((PSD_Force_A[2]-32768) + (PSD_Force_B[2]-32768));
  dist_x = Calibration_Factors[0]*float(PSD_Force_A[0]-32768) + Calibration_Factors[1] * float(PSD_Force_B[0]-32768);
  dist_y = Calibration_Factors[2]*float(PSD_Force_A[1]-32768) - Calibration_Factors[3] * float(PSD_Force_B[1]-32768);
  if (trap==0){

    // Move A to reduce the distance between A and B
    //----------------------AX------------------------
    DAC_pos = (DAC_AX[1] << 8) | DAC_AX[2];
    // Fixing risk of overflow.
    int movement = int(local_align_fac*float(dist_x));
    if (long(DAC_pos + movement) > 65535){
        DAC_pos = 65535;
    }
    else if (long(DAC_pos + movement)<0){
      DAC_pos = 0;
    }
    else{
      DAC_pos += movement;
    }
    DAC_AX[1] = (DAC_pos >> 8) & 0xFF;
    DAC_AX[2] =  DAC_pos & 0xFF;

    //-----------------------AY------------------------    
    DAC_pos = (DAC_AY[1] << 8) | DAC_AY[2];

    // Fixing risk of overflow.
    movement = int(local_align_fac*float(dist_y));
    if (long(DAC_pos - movement) > 65535){
        DAC_pos = 65535;
    }
    else if (long(DAC_pos - movement) < 0){
      DAC_pos = 0;
    }
    else{
      DAC_pos -= movement;
    }

    DAC_AY[1] = (DAC_pos >> 8) & 0xFF;
    DAC_AY[2] =  DAC_pos & 0xFF;

    DAC_AX_target = ((int32_t)((DAC_AX[1]  << 8) | DAC_AX[2] )) << 4;  // Ensuring 32-bit result
    DAC_AY_target = ((int32_t)((DAC_AY[1]  << 8) | DAC_AY[2] )) << 4;  // Ensuring 32-bit result

  }
  else{
    //------------------BX-----------------------------
    
    DAC_pos = (DAC_BX[1] << 8) | DAC_BX[2];
    // Fixing risk of overflow.
    int movement = int(local_align_fac*float(dist_x));
    if (long(DAC_pos + movement) > 65535){
        DAC_pos = 65535;
    }
    else if (long(DAC_pos + movement)<0){
      DAC_pos = 0;
    }
    else{
      DAC_pos += movement;
    }
    DAC_BX[1] = (DAC_pos >> 8) & 0xFF;
    DAC_BX[2] =  DAC_pos & 0xFF;

    //------------------BY-----------------------------
    DAC_pos = (DAC_BY[1] << 8) | DAC_BY[2];
    
    // Fixing risk of overflow.
    movement = int(local_align_fac*float(dist_y));

    if (long(DAC_pos + movement) > 65535){
        DAC_pos = 65535;
    }
    else if (long(DAC_pos + movement) < 0){
      DAC_pos = 0;
    }
    else{
      DAC_pos += movement;
    }
    DAC_BY[1] = (DAC_pos >> 8) & 0xFF;
    DAC_BY[2] =  DAC_pos & 0xFF;

    DAC_BX_target = ((int32_t)((DAC_BX[1]  << 8) | DAC_BX[2] )) << 4;  // Ensuring 32-bit result
    DAC_BY_target = ((int32_t)((DAC_BY[1]  << 8) | DAC_BY[2] )) << 4;  // Ensuring 32-bit result

  }
}

void constant_speed_move(uint8_t DAC_DATA[], uint16_t stepsize, uint16_t limits[]){
  /*
  Moves the trap in DAC_data between upper limits[0] and lower limits[1] on the movement range
  in steps of stepsize. 
  */
  
  DAC_pos = ((DAC_DATA[1] << 8) | DAC_DATA[2]);

  if (position_move_dir == 0) {
      // Move forward
      DAC_pos += stepsize;
      if (DAC_pos >= limits[0]) {
        // Removed the limit check to ensure that we can start from any position
        position_move_dir = 1;
      }
  }
  else {
      DAC_pos -= stepsize;
      if (DAC_pos <= limits[1]) { // The second condition checks for underflow.
        position_move_dir = 0;
      }
  }

  DAC_DATA[1] = (DAC_pos >> 8) & 0xFF;
  DAC_DATA[2] = DAC_pos & 0xFF;

}


void constant_force_protocol(uint8_t DAC_DATA[], uint16_t target_force, int current_force, uint8_t axis){
  force_difference = int(CONSTANT_FORCE_FAC*(float(target_force-32768) - float(current_force-32768))); 
  DAC_pos = ((DAC_DATA[1] << 8) | DAC_DATA[2]);

  // Depending on the axis we should update the DAC position differently.
  if (axis==1){
    force_difference *= -1;
  }

  if (long(DAC_pos + force_difference) > 64000){
      DAC_pos = 64000;
  }
  else if (long(DAC_pos + force_difference) < 1000){
    DAC_pos = 1000;
  }
  else{
    DAC_pos += force_difference;
  }
  
  DAC_DATA[1] = (DAC_pos >> 8) & 0xFF;
  DAC_DATA[2] = DAC_pos & 0xFF;

}

void constant_speed_move_force_lims(uint8_t DAC_DATA[], uint16_t stepsize, uint16_t force_reading_limits[], uint8_t axis){
  /*
  Currently moves in one direction until a force threshold is exceeded or a position limit is reached, position limit is fixed.
  */
  DAC_pos = ((DAC_DATA[1] << 8) | DAC_DATA[2]);

  if (axis == 0||axis==2) {
      // Move forward in x or y by increasing the value of the reading, 0 for x, 2 for y
      if (DAC_pos <= 62000 && !force_limit_reached) {
        DAC_pos += stepsize;
      }
      
  }
  else{
      // move backwards, 1 for x, 3 for y.
      if (DAC_pos >= 2000 && !force_limit_reached) {
        DAC_pos -= stepsize; 
      }      
  }

  DAC_DATA[1] = (DAC_pos >> 8) & 0xFF;
  DAC_DATA[2] = DAC_pos & 0xFF;
}


void constant_speed_move_force_lims_reverse(uint8_t DAC_DATA[], uint16_t stepsize, uint16_t force_reading_limits[], uint8_t axis){
  /*
   Currently moves in one direction until a force threshold is exceeded or a position limit is reached, position limit is fixed.
  */

  DAC_pos = ((DAC_DATA[1] << 8) | DAC_DATA[2]);

  if (axis == 0||axis==2) {
      // Move forward in x or y by increasing the value of the reading, 0 for x, 2 for y
      if (DAC_pos <= 62000 && !force_limit_reached) {
        DAC_pos += stepsize;    
      }
      else if (DAC_pos >1000 && force_limit_reached) {
        DAC_pos -= force_reading_limits[1];    
      }
      
  }
  else{
      // move backwards, 1 for x, 3 for y.
      if (DAC_pos >= 2000 && !force_limit_reached) {
        DAC_pos -= stepsize; 
      }
      if (DAC_pos <= 62000 && force_limit_reached) {
        DAC_pos += force_reading_limits[1]; 
      }
  }

  DAC_DATA[1] = (DAC_pos >> 8) & 0xFF;
  DAC_DATA[2] = DAC_pos & 0xFF;
}

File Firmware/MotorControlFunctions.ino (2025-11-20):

/*
This file contains the necessary functions and definistions for interfacing the motors
*/
#include <Portenta_H7_PWM.h> 

// Define PWM PINS
#define MOTOR_X_PWM D6     // PWM0
#define MOTOR_Y_PWM D2     // PWM4 // won't allow usage of PWM3
#define MOTOR_Z_PWM D0     // PWM6

// Define motor channels pins(for position)

#define MotorXChA PC_15    // GPIO_1
#define MotorXChB PD_4     // GPIO_2
#define MotorYChA PD_5     // GPIO 3
#define MotorYChB PE_3     // GPIO 4
#define MotorZChA PG_3     // GPIO 5
#define MotorZChB PG_10    // GPIO 6

// Motor direction pins
#define Motor_X_dir1 PC_6  //UART0_TX //PWM1 pin   //PREV D4  // works, located at PWM5 pin
#define Motor_X_dir2 PC_7  //UART0_RX //PWM2 pin   //PREV A0
#define Motor_Y_dir1 D3    //PWM 3, PWM3 didn't work as output, unclear why.
#define Motor_Y_dir2 PK_1  //PWM 5
#define Motor_Z_dir1 PJ_7  //PWM7
#define Motor_Z_dir2 PJ_10 //PWM8

// Motor limit pins
#define MOTOR_X_FWD_LIM PH_7
#define MOTOR_X_REV_LIM PH_7
#define MOTOR_Y_FWD_LIM PA_9
#define MOTOR_Y_REV_LIM PA_10
#define MOTOR_Z_FWD_LIM PA_99
#define MOTOR_Z_REV_LIM PA_99

// Fixed parameters
#define MAX_FREQ 10000.0f
#define DUTY_CYCLE_MAX 100.0f
#define DUTY_CYCLE_MIN 3.0f
#define MOVE_THRESHOLD 2

// PID parameters
#define K_P 5000.0f
#define K_I 0.0f 
#define K_D 2000.0f

#define K_P_position 0.08f
#define K_D_position 0.08f
#define NUM_OF_PINS (sizeof(motorPWMPins) / sizeof(uint32_t))
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

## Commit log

2025-04-13 Create firmware folder
    Created the folder for the firmware of the MiniTweezers.
    Is to be run on an arduino portenta.
2025-04-13 PDF schematics for minitweezers
    PDFs containing the schematics of the minitweezers circuitboards
2025-06-30 Update CameraControlsNew.py
    Comments in the code have been edited for better readability.
2025-06-30 Update CameraMeasurementTool.py
    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
2025-06-30 Update LaserController.py
    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
2025-06-30 Update LaserPiezosControlWidget.py
    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
2025-06-30 Update MotorControlWidget.py
    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
2025-09-11 BOM files
    BOM files used for ordering electronics components to the various boards
    [PSD2DACV2_0.xlsx, PiezoAndMotorBoardV1_1.xlsx, PortentaComputeBoardV1_2.xlsx]
2025-09-14 3D printable componets for the pipette puller
    [PullerBottom.stl, PullerClampBlock.stl, PullerMiddle.stl, PullerTop.stl]
2025-09-14 Added component list
    Pipette puller components needed.
    [PipettePullerComponents.xlsx]
2025-09-14 Added a suitable PSU unit
    [PipettePullerComponents.xlsx]
2025-09-17 Chamber assembly images
2025-09-17 capillaries and pipette image update
2025-09-17 pipette mounting
2025-09-17 video of a pipette being pulled
2025-09-17 Update README.md
    Added pipette pulling video
2025-09-19 Update smarttrap_tracker.py
    Modify line 234 to ensure the loaded model is device-independent.
2025-09-19 Update smarttrap_tracker.py
    I modified and added lines 236-242 to initialize a new CNN model in case there is no existing model to load.
2025-09-19 Added the GUI camera example files.
    Examples to test the camera with a GUI
2025-09-19 Add example_camera.ipynb
    This Python notebook tests whether the camera is working by connecting to it and displaying an acquired frame.
2025-09-20 Update README.md
    Updates to chamber installation, still missing the chamber pictures
2025-09-20 Chamber mounting images
2025-09-20 Chamber mounted and glued
2025-09-20 Update README.md
    Updated the chamber installation with a few pictures
2025-09-23 Assembly video
2025-10-13 Component list for the Tweezers instrument
    Component list for the Tweezers instrument and the controller power supply.
    [ComponentList.xlsx]
2025-10-13 Files for the tweezers
    [laser base mill cut7.dxf]
2025-10-13 Animated pipette puller assembly
2025-10-15 Controller board files
2025-10-15 3D printable files for the controller stand
    [ControllerStand.stl, PCB_spacers.stl]
2025-10-20 Add link to FullAssembly video in README
    Updated the assembly instructions to include a link to the FullAssembly video.
2025-12-05 Update README with copyright and usage terms
    Added copyright and usage information for materials developed by Steve Smith and the Bustamante Group.
2026-02-04 Updates to various components
    [Aperture Iris Button updated.step, Chamber holder pin updated.step, Filter holder disc-updated.step, PSD holder handle updated.step]
2026-02-04 Update README with material details and 3D printing infoU
    Added material specifications for certain components and 3D printing instructions.
2026-02-04 Revise material list and 3D printing instructions
    Updated material specifications for components and added details for 3D printing.
